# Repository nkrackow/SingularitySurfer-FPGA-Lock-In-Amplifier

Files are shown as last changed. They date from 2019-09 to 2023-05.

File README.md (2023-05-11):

# SingularitySurfer: An FPGA Lock-In Amplifier
Repository of an FPGA based DSP Lock-In Amplifier.

## Fotos:
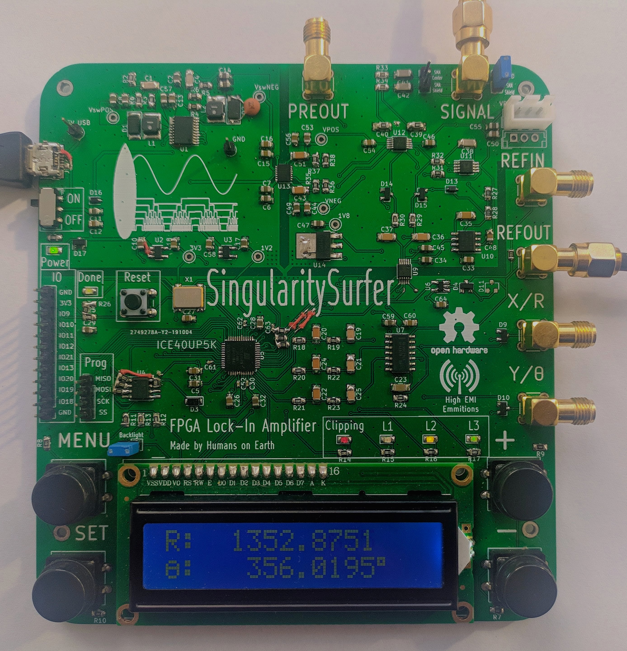
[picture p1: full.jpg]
Board front

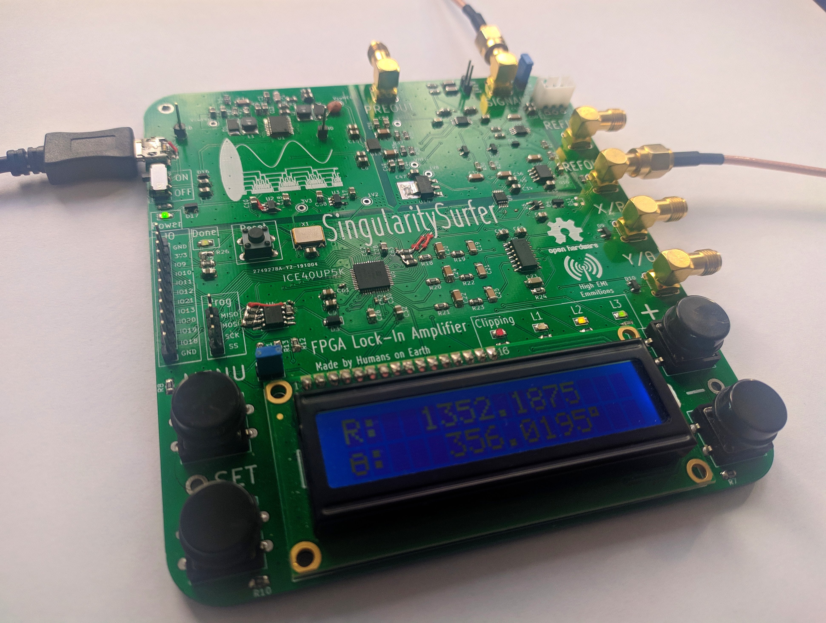
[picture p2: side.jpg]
Board sinde

Measuring the change of phase due to changing the distance of two speakers (of which one functions as a crappy microphone):
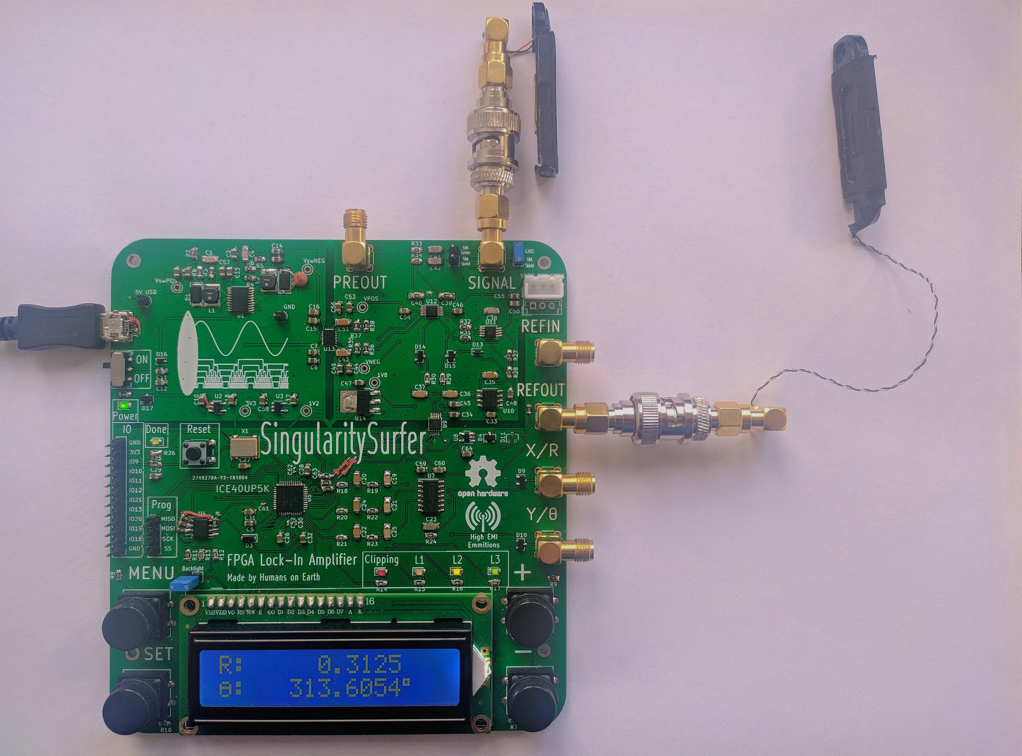
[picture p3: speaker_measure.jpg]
Measuring the change of phase due to the distance of two speakers (of which one functions as a crappy microphone)


## Block Diagram:
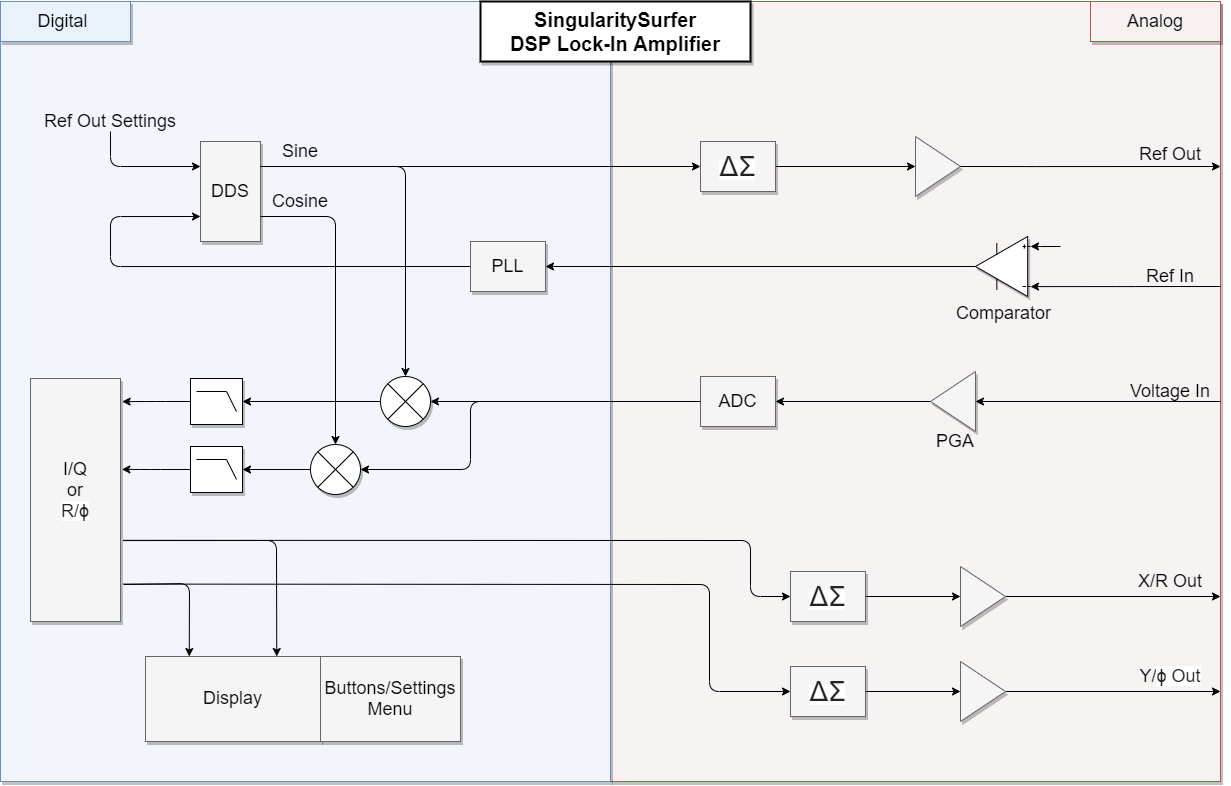
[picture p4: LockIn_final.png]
Block Diagram


## Overview:
Lock-In amplifiers are a very useful tool in many physics and bio experiments where your signal of interest might be covered by a lot of noise and interference. It does so by effectively correlating out the signal of interest. As analog components are always subject to noise, drift and non-linearities, performance in a DSP Lock-In can be far superior.
The project leverages the affordable ICE40 FPGA with its fully open source toolchain to implement the digital signal processing. Analog components are implemented in a manner that strikes a balance between performance and cost. As the analog frontend mostly determines the overall performance, a focus was put on its implementation. The total BOM cost is below 70€.
The SingularitySurfer was developed as a personal learning platform that I share so others can get design ideas and see my approach. It does not intend to give reference designs or to teach the subject. 
Cores from other people:
* CORDIC: https://opencores.org/projects/verilog_cordic_core
* SPI flash reader: https://github.com/smunaut/ice40-playground/tree/master/cores/spi_flash
* 2x16 character display driver: https://opencores.org/projects/wb_lcd

The next sections will describe the features of the various sub-systems, their development and the design decisions made.

## Digital architecture:
All of the FPGA cores run at a 36MHz base clock and the numeric oscillator, DDS, PLL and DACs also run at this sample frequency. However the ADC samples at 900kHz and the digital filters further downsample the signal by a factor of 1024. The DDS and the ADC produce signed 16 bit signals, while the output of the multipliers and filters are signed 32 bit. The phase signals from the PLL and oscillator are 18 bit. Due to FPGA LUT constraints, the CORDIC core only uses signed 16bit precision and the algorithm is terminated after 9 iterations. Most of the cores, especially the CORDIC core, make use of pipelining to maintain the 36MHz clock. The full design takes up about 85% of the FPGA LUTs.

## FPGA:
The Lattice ICE40UP5K is an ideal platform for a small DSP project like this. It offers:
* sufficient LUTs for all of the wiring, UI, display and housekeeping
* 8 16x16 hardware multipliers for signal processing
* 1Mbit of internal SRAM for storing a high fidelity sine lookup table
* QFP package which is easily soldered by hand
* affordable price at just 5€
* fully open source toolchain!

## Analog frontend:
As all of the digital signal processing is deterministic and can be upgraded at a later point, the Lock-In’s performance is ultimately determined by the analog frontend. The goal is to transfer the signal into the digital domain with little disturbance. This requires high dynamic range, low noise and high linearity. But as cost was also a factor in the development, compromises had to be made. The design employs:
* ADC: MCP33131D, 1MSps, 16bit, 91.3dB SNR 
* Voltage reference: REF5050, low noise, low drift
* PGA: AD8253, 0-60dB gain, low distortion, low noise, instrumentation amplifier
* OpAmp: AD8675, low noise
* Voltage regulator: LT3032-15, dual +-15V, low noise

At the input there is a 100kHz RC lowpass and the ADC AA filter is tuned to 100kHz as well. The PGA doubles as the ADC driver, using the AD8675 to make the signal differential. This setup was used to cut the cost of a dedicated ADC driver. Unfortunately it does limit performance, as it does introduce some distortion due to the PGA output not being fast enough to drive the ADC (which is not critical as distortion is essentially the same as noise well outside the passband of the digital lowpass). Broadband noise from the analog components was below the quantization noise and therefore not visible at the ADC output.

## DDS and numeric oscillator:
The direct digital synthesis core generates a digital representation of a sinusoidal using a 1/4 sinus look-up table stored in the 1Mbit SRAM. The other 3/4 of the sine and the cosine can be easily generated from the first 1/4 using symmetries. Therefore a high fidelity, 16bit amplitude, 18bit phase representation of the sinusoidals can be generated. When using an external reference signal, the DDS uses the phase of the digital PLL locked to the external reference signal. When generating its own reference signal, a numeric oscillator with an internal 32bit phase accumulator is employed. 
In order to avoid spurious tones in the output spectrum of the DDS when using the internal oscillator, dithering of the last phase-bit is applied using a linear-feedback shift register. Unfortunately the ICE40 SRAM blocks don't support initial values in the FPGA bitstream. Therefore the look-up table is permanently stored in the external SPI flash and loaded into SRAM after every startup.

## DAC:
As the Lock-In’s performance is not dependent on the output reference signal (as long as it contains a strong spectral component exactly at the reference frequency and other spectral components are masked by the noise added in the DUT), a basic sigma-delta DAC is used. Same goes for the X/R and Y/Theta "baseband" outputs, as they are essentially just DC (however DC accuracy has to be considered here) . The sigma-delta DACs require just a single FPGA pin and a passive second order lowpass with buffered output as external hardware in order to generate analog signals. Inside the FPGA the DAC uses a basic first-order sigma-delta modulator. With a modulator frequency of 36 MHz and 100kHz lowpass cutoff, the SNR is still better than 60dB. However switching many single-ended FPGA pins at these frequencies might lead to high EMI emissions. This was tried to be avoided by placing the lowpass filter close to the FPGA pins.

## PLL *(experimental)*:
The all-digital PLL gets a clean digital input signal by the use of a Schmitt-Trigger at the reference input. It uses a 32bit phase accumulator and 17bit phase increment word which leads to good phase precision. The DP controller can update the phase increment word without the need for multipliers by simply bit shifting the error signals. The controller can therefore only be tuned very coarsely which was done by simple trial and error. With this setup the controller can lock and track any reference signal between 500Hz and 100kHz. However it can get stuck in "limbo" with an aperiodic input signal and needs a reset to recover.

## Multipliers and CIC filter:
Twor 16x16 hardware multipliers directly "mix" the incoming ADC samples with the sine/cosine signals from the DDS core. The output is therefore a 32bit signal at ADC sampling speed. 
This signal needs to be lowpass filtered to get rid of the undesired mixing products, ideally with a very low cutoff frequency (i.e. long time-constant). At ADC sampling speed this would require a lot of memory. But as the desired signal is bandlimited to a very low frequency (10s or 100s of Hz), a high sampling rate is unnecessary. A cascaded integrator comb (CIC) filter can downsample and lowpass filter the signal at the same time. Furthermore the cutoff frequency can easily be changed in powers of two and it doesn’t require hardware multipliers. 
The downside is that the frequency response is far from an ideal lowpass. Fortunately in the case of the lock-in, this is not critical, as the cutoff frequencies are so low and the upper mixer output products are far higher than fc (it will just let more noise through which can be counteracted by a longer filter time constant). In fact right now, only a single IC stage is used in the SingularitySurfer, as there is already not enough memory for a second integrator. A good improvement would be to follow the CIC with an IIR filter using the remaining hardware multipliers.

## *(update 2020)* Multiplier less IIR filter
The SingularitySurfer was recently upgraded with a better lowpass using a very clever first order IIR filter. It uses the fact that you can multiply by a number close to 1 with bitshifting in hardware. E.g x*(15/16) can be accomplished via x-(x>>4). See [PYTHON_FILTER](https://github.com/SingularitySurfer/SingularitySurfer-FPGA-Lock-In-Amplifier/tree/master/PYTHON_FILTER) for a python demonstration.

## CORDIC:
The CORDIC algorithm computes the angle and magnitude of the sine and cosine signals. The original core by Dale Dickard was extended to support full 360 degree rotation and modified to fit into the remaining ICE40 logic. 

## Display and UI:
The display allows direct monitoring of the Lock-In outputs and user interaction with the UI. The UI is controlled via four buttons on the side of the display. This way the user can navigate through the device settings:
* Filter time constant: between 2^0 and 2^15 milliseconds
* PGA gain: 0dB, 20dB, 40dB, 60dB
* Internal/external reference 
* Internal reference frequency: 500Hz, 1kHz, 2kHz, 5kHz, 10kHz, 20kHz, 50 kHz, 100kHz
*  Internal reference output amplitude: 0.45V, 0.9V, 1.6V, 3.3V (peak to peak)

The signal monitoring can easily be switched between X/Y and R/θ view. The display is a simple 2x16 character LCD display with built-in character ROM. Unfortunately, the maximum update rate of such a display is about 2Hz. A higher update rate would lead to a more direct user feedback when monitoring signals. The logic to drive the display, show text, decimal numbers, etc., is actually not trivial and a small embedded processor could be a better idea in a future project.

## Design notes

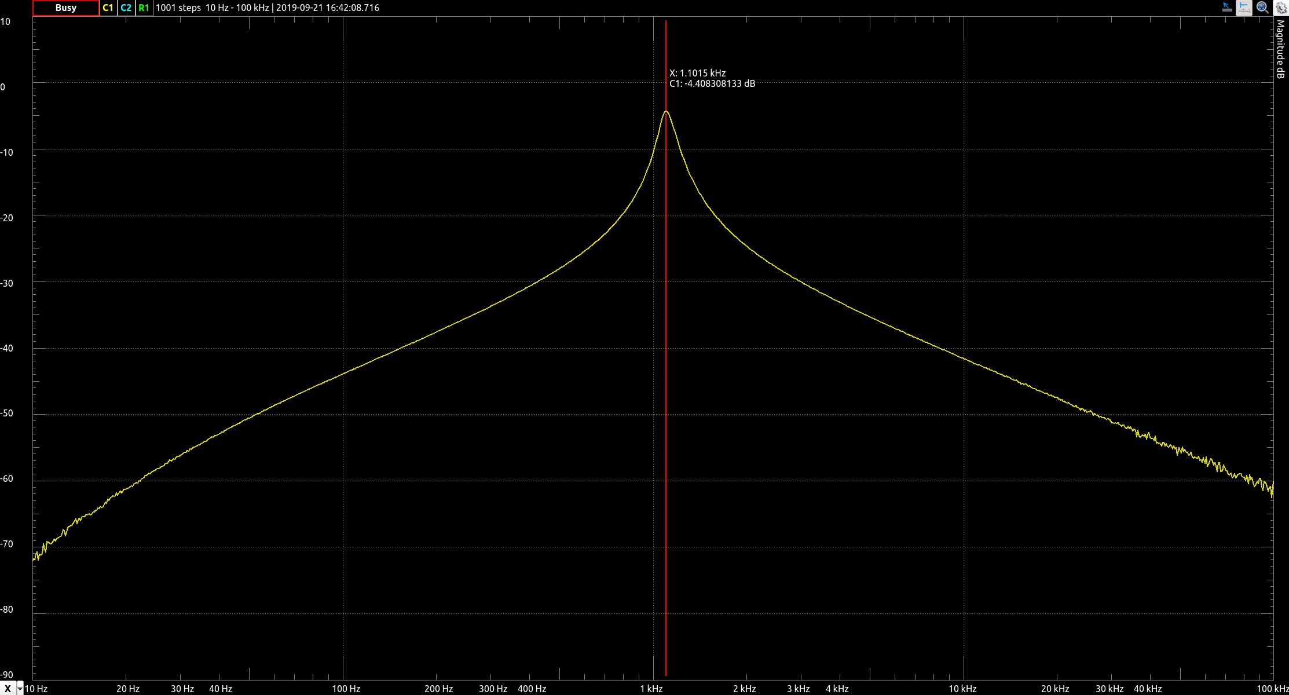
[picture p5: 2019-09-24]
WAVEFORMS/Screenshot from 2019-09-21 16-47-09.png

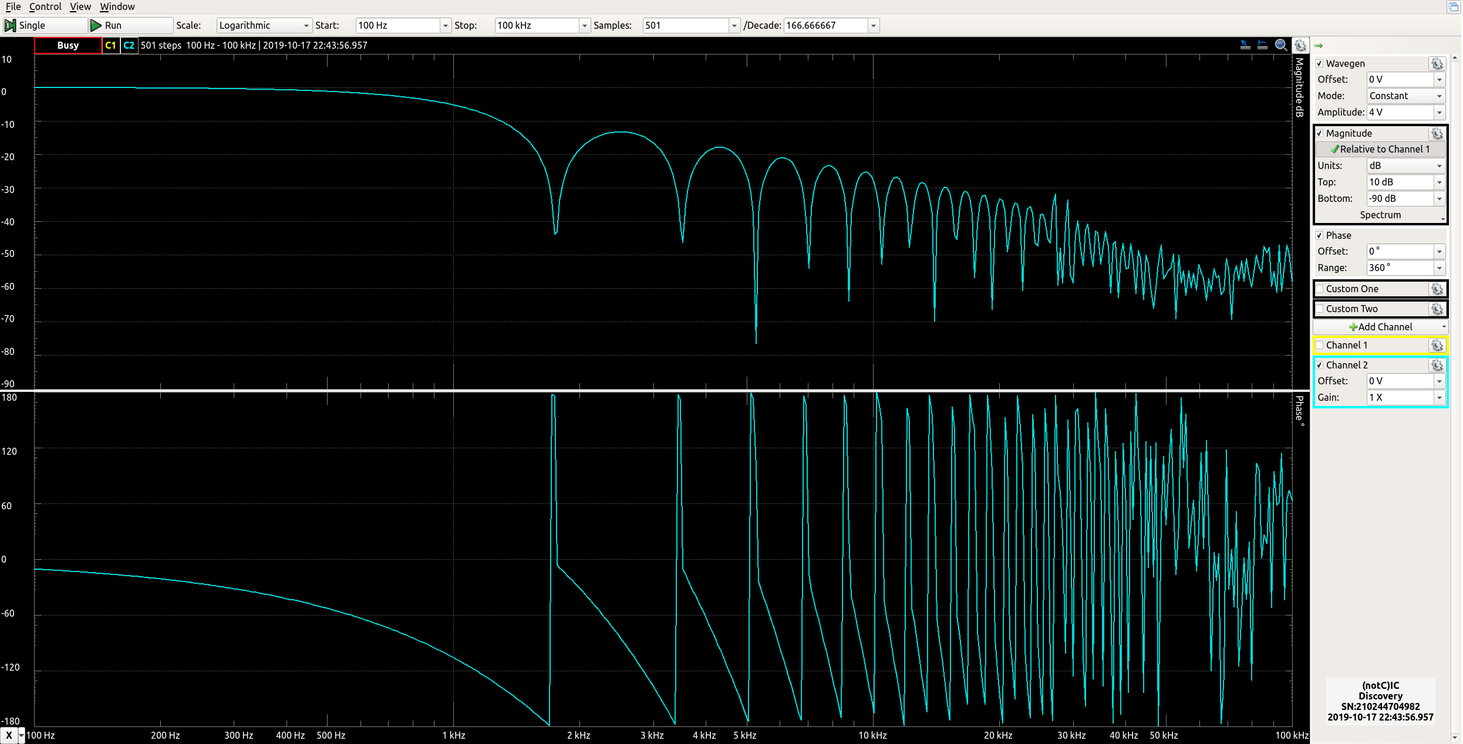
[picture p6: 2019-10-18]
WAVEFORMS/notC_I_C_filter.png

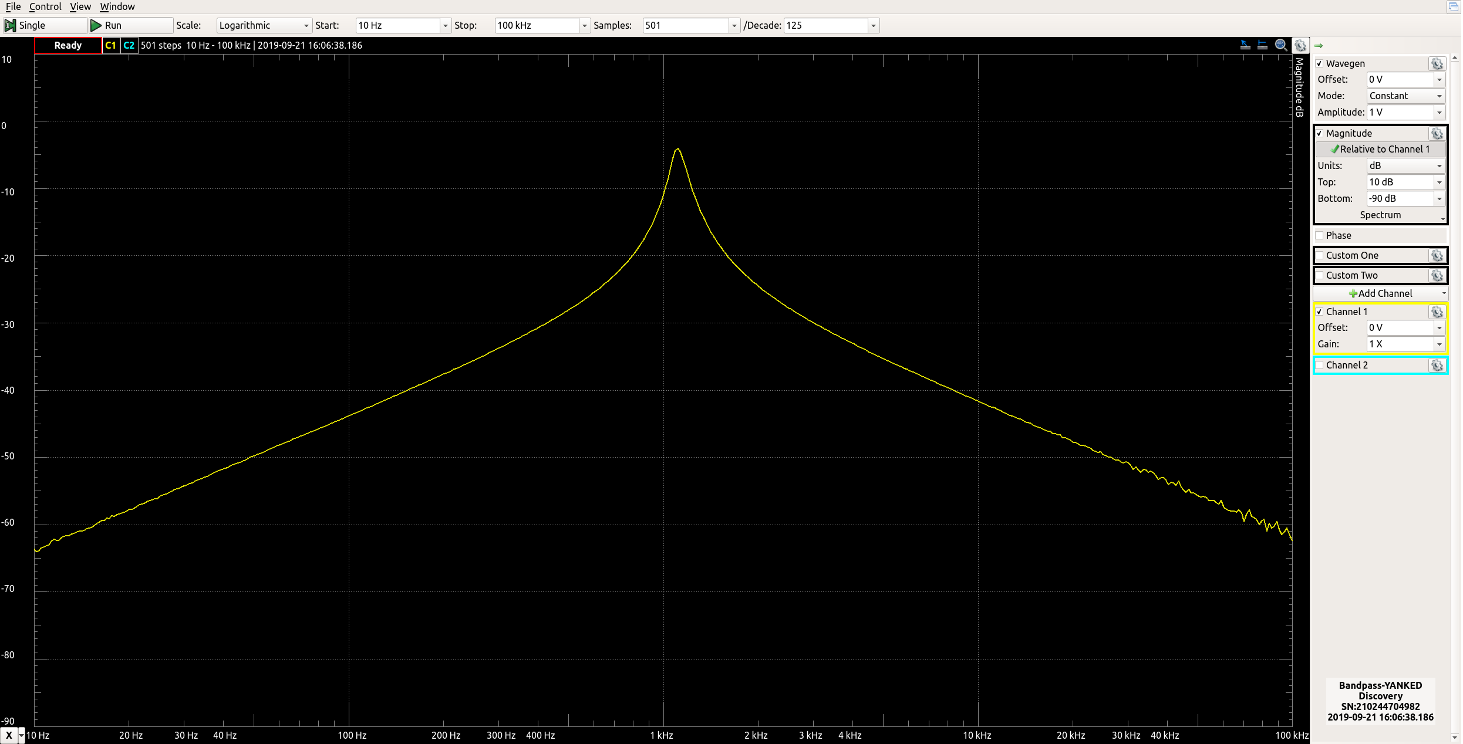
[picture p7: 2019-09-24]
WAVEFORMS/Bandpass-BAAM.png

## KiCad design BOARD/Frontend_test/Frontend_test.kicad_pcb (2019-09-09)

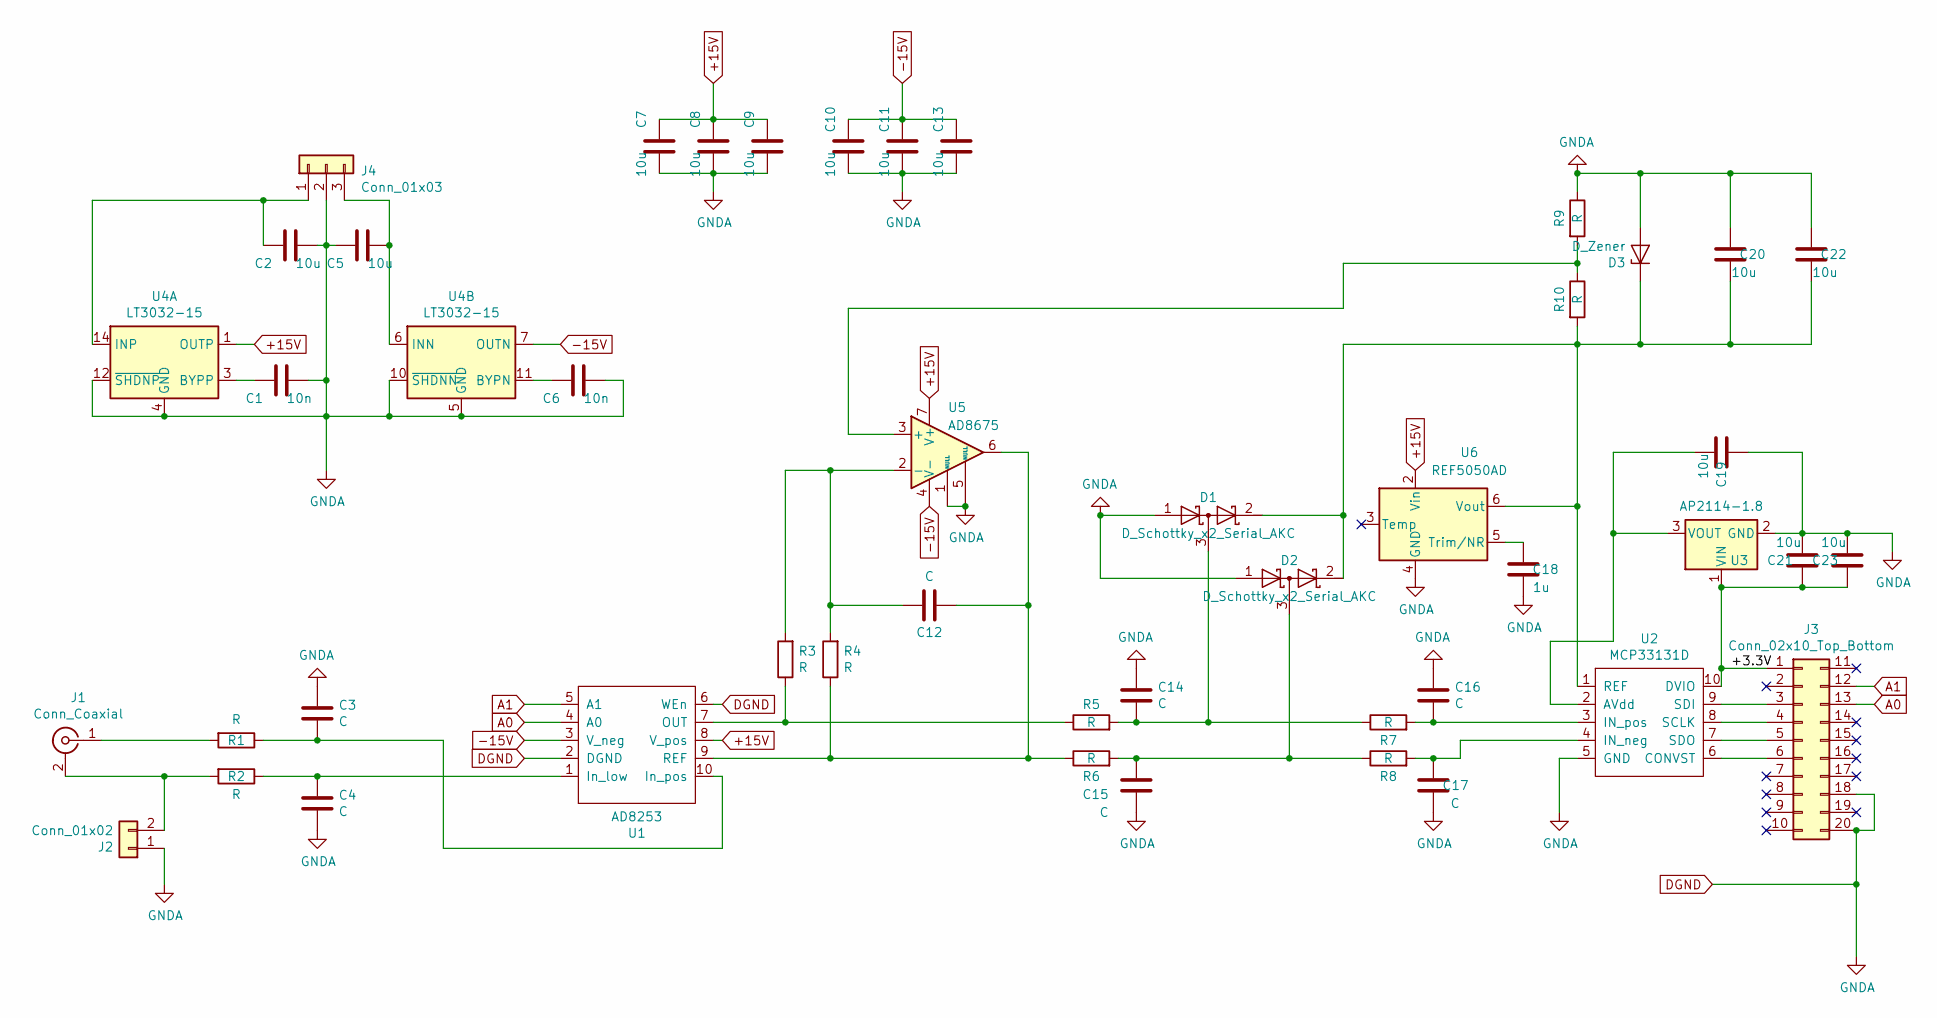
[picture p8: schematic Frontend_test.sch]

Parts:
C1, C6: 10n; C_1206_3216Metric_Pad1.42x1.75mm_HandSolder
C2, C5, C7, C8, C9, C10, C11, C13, C19, C20, C21, C22, C23: 10u; C_0805_2012Metric_Pad1.15x1.40mm_HandSolder
C3, C4, C12, C14, C15, C16, C17: C; C_1206_3216Metric_Pad1.42x1.75mm_HandSolder
C18: 1u; C_1206_3216Metric_Pad1.42x1.75mm_HandSolder
D1, D2: D_Schottky_x2_Serial_AKC; SOT-23
D3: D_Zener; D_SOD-323
J1: Conn_Coaxial; SMA_Molex_73251-2200_Horizontal
J2: Conn_01x02; PinHeader_1x02_P2.54mm_Vertical
J3: Conn_02x10_Top_Bottom; PinHeader_2x10_P2.54mm_Vertical
J4: Conn_01x03; JST_EH_B3B-EH-A_1x03_P2.50mm_Vertical
R1, R2, R3, R4, R5, R6, R7, R8, R9, R10: R; R_0805_2012Metric_Pad1.15x1.40mm_HandSolder
U1: AD8253; MSOP-10_3x3mm_P0.5mm
U2: MCP33131D; MSOP-10_3x3mm_P0.5mm
U3: AP2114-1.8; SOT-223
U4: LT3032-15; DFN-14-1EP_split_bottom_pad_3x4mm_P0.5mm_EP1.7x3.3mm
U5: AD8675; MSOP-8_3x3mm_P0.65mm
U6: REF5050AD; SOIC-8_3.9x4.9mm_P1.27mm

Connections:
+15V: C7.2, C8.2, C9.2, U1.8 (V_pos), U4.1 (OUTP), U5.7 (V+), U6.2 (Vin)
-15V: C10.2, C11.2, C13.2, U1.3 (V_neg), U4.7 (OUTN), U5.4 (V-)
/+3.3V: C21.2, C23.2, J3.1, U2.10 (DVIO), U3.1 (VIN)
A0: J3.13, U1.4 (A0)
A1: J3.12, U1.5 (A1)
DGND: C1.1, C2.1, C3.1, C4.2, C5.2, C6.1, C7.1, C8.1, C9.1, C10.1, C11.1, C13.1, C14.1, C15.1, C16.1, C17.1, C18.1, C19.2, C20.2, C21.1, C22.2, C23.1, D1.1 (A), D2.1 (A), D3.2 (A), J2.1, J3.18, J3.20, J4.2, R9.1, U1.2 (DGND), U1.6 (WEn), U2.5 (GND), U3.2 (GND), U4.4 (GND), U4.5 (GND), U4.10 (~SHDNN), U4.12 (~SHDNP), U5.1 (NULL), U5.5 (NULL), U6.4 (GND)
unnamed: C1.2, U4.3 (BYPP)
unnamed: C2.2, J4.1, U4.14 (INP)
unnamed: C3.2, R1.1, U1.10 (In_pos)
unnamed: C4.1, R2.1, U1.1 (In_low)
unnamed: C5.1, J4.3, U4.6 (INN), U4.9 (INN)
unnamed: C6.2, U4.11 (BYPN)
unnamed: C12.1, R4.1, R6.1, U1.9 (REF), U5.6
unnamed: C12.2, R3.2, R4.2, U5.2 (-)
unnamed: C14.2, D1.3 (common), R5.2, R7.1
unnamed: C15.2, D2.3 (common), R6.2, R8.1
unnamed: C16.2, R7.2, U2.3 (IN_pos)
unnamed: C17.2, R8.2, U2.4 (IN_neg)
unnamed: C18.2, U6.5 (Trim/NR)
unnamed: C19.1, U2.2 (AVdd), U3.3 (VOUT)
unnamed: C20.1, C22.1, D1.2 (K), D2.2 (K), D3.1 (K), R10.2, U2.1 (REF), U6.6 (Vout)
unnamed: J1.1 (In), R1.2
unnamed: J1.2 (Ext), J2.2, R2.2
unnamed: J3.3, U2.9 (SDI)
unnamed: J3.4, U2.8 (SCLK)
unnamed: J3.5, U2.7 (SDO)
unnamed: J3.6, U2.6 (CONVST)
unnamed: R3.1, R5.1, U1.7 (OUT)
unnamed: R9.2, R10.1, U5.3 (+)

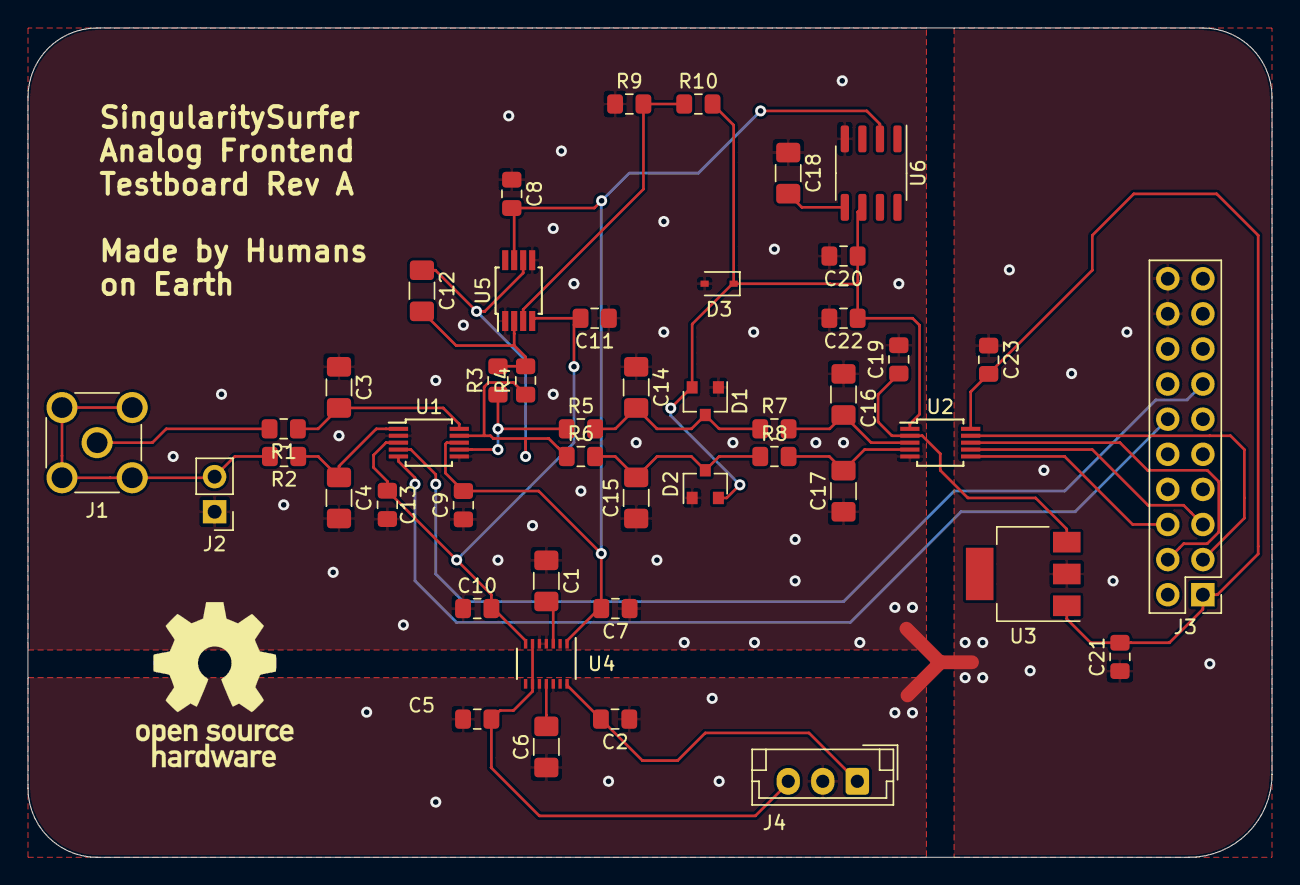
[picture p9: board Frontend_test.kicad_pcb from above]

Board: 2 copper layers, 90.0 x 60.0 mm, 46 parts (0 on the bottom side), 29 nets.

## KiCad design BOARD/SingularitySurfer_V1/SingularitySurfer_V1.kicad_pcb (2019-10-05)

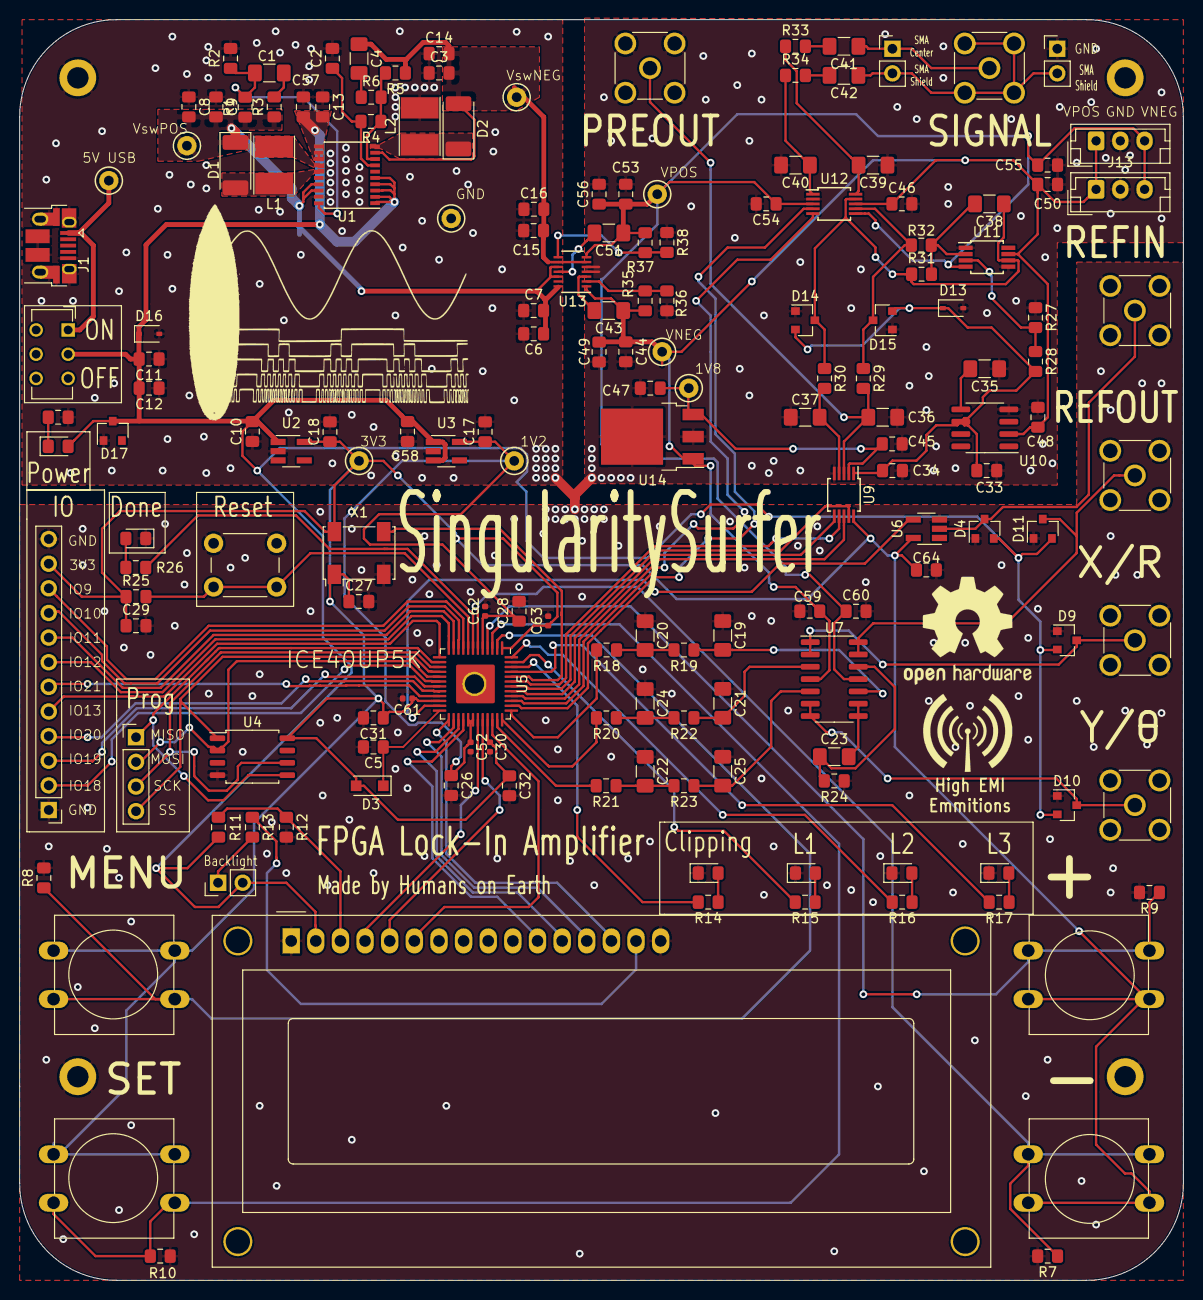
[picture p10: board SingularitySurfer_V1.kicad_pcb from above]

Board: 2 copper layers, 120.0 x 130.0 mm, 171 parts (0 on the bottom side), 99 nets.

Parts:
 : TestPoint; TestPoint_Keystone_5000-5004_Miniature
 #2,  #3,  #4,  #5: MountingHole_2.2mm_M2_DIN965_Pad
 #6: Conn_01x02_Male; PinHeader_1x02_P2.54mm_Vertical
 #7: Conn_01x12; PinHeader_1x12_P2.54mm_Vertical
 #8: Conn_01x04_Male; PinHeader_1x04_P2.54mm_Vertical
 #9,  #12,  #13,  #14,  #15,  #16,  #17,  #18: TestPoint; TestPoint_Keystone_5000-5004_Miniature
 #10: R; R_0805_2012Metric_Pad1.15x1.40mm_HandSolder
 #11: Conn_01x03; JST_EH_B3B-EH-A_1x03_P2.50mm_Vertical
 #19,  #20,  #21,  #22,  #23,  #24: LED; LED_0805_2012Metric_Pad1.15x1.40mm_HandSolder
 #25,  #27,  #30,  #31,  #32,  #33: Conn_Coaxial; SMA_Molex_73251-2200_Horizontal
 #26: SW_Push; SW_PUSH_6mm
 #28,  #29: Conn_01x02; PinHeader_1x02_P2.54mm_Vertical
 #34: WC1602A
 #35: SW_DIP_x01; SW_CuK_JS202011AQN_DPDT_Angled
+1: SW_Push; SW_PUSH-12mm
-1: SW_Push; SW_PUSH-12mm
C1, C4, C19, C20, C21, C22, C23, C24, C25, C36, C37, C38, C39, C40, C41, C42, C43, C51: C; C_1206_3216Metric_Pad1.42x1.75mm_HandSolder
C2, C3, C5, C6, C7, C8, C9, C10, C11, C12, C13, C14, C15, C16, C17, C18, C26, C27, C28, C29, C31, C32, C44, C45, C46, C47, C48, C49, C50, C53, C54, C55, C56, C57, C58, C59, C60, C64: C; C_0805_2012Metric_Pad1.15x1.40mm_HandSolder
C30, C52, C61, C62, C63: C; C_0402_1005Metric
C33, C34: 10u; C_0805_2012Metric_Pad1.15x1.40mm_HandSolder
C35: 1u; C_1206_3216Metric_Pad1.42x1.75mm_HandSolder
D1, D2: D; D_2010_5025Metric_Pad1.52x2.65mm_HandSolder
D3: D; D_SOD-123F
D4, D9, D10, D11, D14, D15, D17: D_Schottky_x2_Serial_AKC; SOT-23
D13, D16: D_Zener; D_SOD-323
J1: USB_B_Micro; USB_Micro-B_Amphenol_10103594-0001LF_Horizontal
J13: Conn_01x03; JST_EH_B3B-EH-A_1x03_P2.50mm_Vertical
L1, L2: INDUCTOR; L_Taiyo-Yuden_NR-40xx_HandSoldering
MENU1: SW_Push; SW_PUSH-12mm
R1, R2, R3, R4, R5, R6, R7, R8, R9, R10, R11, R12, R13, R14, R15, R16, R17, R18, R19, R20, R21, R22, R23, R24, R25, R26, R27, R28, R29, R30, R31, R32, R33, R34, R35, R36, R37, R38: R; R_0805_2012Metric_Pad1.15x1.40mm_HandSolder
SET1: SW_Push; SW_PUSH-12mm
U1: BD81870EFV; SSOP-20_4.4x6.5mm_P0.65mm
U2: MIC5504-3.3YM5; SOT-23-5_HandSoldering
U3: TLV70212_SOT23-5; SOT-23-5_HandSoldering
U4: W25Q32JVSS; SOIC-8_5.23x5.23mm_P1.27mm
U5: ICE40UP5K-SG48ITR; QFN-48-1EP_7x7mm_P0.5mm_EP5.6x5.6mm
U6: 74LVC1G17; SOT-23-5_HandSoldering
U7: OPA1679; SOIC-14_3.9x8.7mm_P1.27mm
U9: MCP33131D; MSOP-10_3x3mm_P0.5mm
U10: REF5050AD; SOIC-8_3.9x4.9mm_P1.27mm
U11: AD8675; MSOP-8_3x3mm_P0.65mm
U12: AD8253; MSOP-10_3x3mm_P0.5mm
U13: LT3032; DFN-14-1EP_split_bottom_pad_3x4mm_P0.5mm_EP1.7x3.3mm
U14: AP2114-1.8; TO-252-3_TabPin2
X1: DFA-S11; Oscillator_SMD_Fordahl_DFAS11-4Pin_7.0x5.0mm

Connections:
1V2: #12.1, C17.1, C26.1, C28.1, C52.1, C62.1, U3.5, U5.5, U5.29, U5.30
1V8: #16.1, C45.1, C47.1, U9.2, U14.3
3V3: #7.11, #9.1, +1.2, -1.2, C18.1, C27.1, C29.1, C30.1, C31.1, C32.1, C61.1, C63.1, C64.1, D3.2, MENU1.2, R25.1, SET1.2, U2.5, U4.8, U5.1, U5.22, U5.33, U6.5, U9.10, X1.1, X1.4
5V: #6.2, #19.2, #34.2, #35.2, C10.2, C11.2, C12.2, C13.2, C57.2, C58.2, D4.2, D9.2, D10.2, D11.2, D16.1, D17.3, R11.1, U1.1, U1.2, U1.3, U1.4, U1.5, U1.11, U1.12, U1.13, U2.1, U3.1, U3.3
+8V: #11.1, #15.1, C43.1, C44.1, C46.1, C48.1, C49.1, C50.1, C59.1, J13.1, R35.2, U7.4, U10.2, U11.7, U12.8, U13.1, U14.1
-8V: #11.3, #13.1, C51.1, C53.1, C54.1, C55.1, C56.1, C60.1, J13.3, R37.2, U7.11, U11.4, U12.3, U12.6, U13.7
/Power/VNEG: #14.1, C3.2, C4.1, C14.2, C15.2, C16.2, D2.2, R5.1, U1.9, U13.6, U13.9
A0: U5.38, U12.4
A1: U5.39, U12.5
CDONE: R26.2, U5.7
CONVST: U5.41, U9.6
GND: .1, #2.1, #3.1, #4.1, #5.1, #7.1, #7.12, #10.1, #11.2, #20.1, #21.1, #22.1, #23.1, #24.1, #25.2, #26.1, #28.1, #30.2, #31.2, #32.2, #33.2, #34.1, #34.16, C2.2, C3.1, C5.2, C6.1, C7.1, C8.1, C9.1, C10.1, C11.1, C12.1, C13.1, C14.1, C15.1, C16.1, C17.2, C18.2, C19.1, C20.1, C21.1, C22.1, C24.1, C25.1, C26.2, C27.2, C28.2, C29.2, C30.2, C31.2, C32.2, C33.2, C34.2, C35.1, C36.1, C37.1, C39.1, C40.2, C44.2, C45.2, C46.2, C47.2, C48.2, C49.2, C50.2, C52.2, C53.2, C54.2, C55.2, C56.2, C57.1, C58.1, C59.2, C60.2, C61.2, C62.2, C63.2, C64.2, D4.1, D9.1, D10.1, D11.1, D13.2, D14.1, D15.1, D16.2, D17.1, J1.5, J1.6, J13.2, L2.2, R2.2, R7.2, R8.2, R9.2, R10.2, R12.2, R24.1, R27.1, R36.1, R38.1, U1.16, U1.19, U2.2, U3.2, U4.4, U5.49, U6.3, U9.5, U10.4, U11.1, U11.5, U12.2, U13.4, U13.5, U14.2, X1.2
unnamed: +1.1, R9.1, U5.4
unnamed: -1.1, R7.1, U5.6
unnamed: C1.1, R3.2
unnamed: C1.2, R1.2, R2.1, U1.20
unnamed: C2.1, R4.2, U1.7
unnamed: C4.2, R6.1
unnamed: C5.1, D3.1, U5.24
unnamed: C19.2, R19.1, U7.10
unnamed: C20.2, R18.1, R19.2
unnamed: C21.2, R22.1, U7.3
unnamed: C22.2, R21.1, R23.2
unnamed: C23.1, R24.2, U7.12
unnamed: C23.2, U7.8, U7.9
unnamed: C24.2, R20.1, R22.2
unnamed: C25.2, R23.1, U7.5
unnamed: C33.1, C34.1, D13.1, D14.2, D15.2, R28.2, U9.1, U10.6
unnamed: C35.2, U10.5
unnamed: #25.1, C36.2, R29.2, U9.3
unnamed: C37.2, R30.2, U9.4
unnamed: C38.1, D14.3, R30.1, R31.1, U11.6, U12.9
unnamed: C38.2, R31.2, R32.2, U11.2
unnamed: C39.2, R33.1, U12.10
unnamed: C40.1, R34.1, U12.1
unnamed: #27.1, #29.1, C41.1
unnamed: C41.2, R33.2
unnamed: #27.2, #28.2, #29.2, C42.1
unnamed: C42.2, R34.2
unnamed: C43.2, U13.3
unnamed: C51.2, U13.11
unnamed: D1.2, L1.1, U1.15
unnamed: D2.1, L2.1, U1.10
unnamed: #33.1, D4.3, U6.2
unnamed: #24.2, R14.1
unnamed: #23.2, R15.1
unnamed: #22.2, R16.1
unnamed: #21.2, R17.1
unnamed: #31.1, D9.3, U7.1, U7.2
unnamed: #30.1, D10.3, U7.6, U7.7
unnamed: #32.1, D11.3, U7.13, U7.14
unnamed: #20.2, R26.1
unnamed: D15.3, R29.1, R32.1, U12.7
unnamed: #10.2, #19.1
unnamed: #34.3, R11.2, R12.1
unnamed: #34.4, U5.31
unnamed: #34.5, U5.32
unnamed: #34.6, U5.34
unnamed: #34.11, U5.28
unnamed: #34.12, U5.27
unnamed: #34.13, U5.26
unnamed: #34.14, U5.25
unnamed: #34.15, R13.1
unnamed: #17.1, #35.1, J1.1
unnamed: #8.1, U4.5, U5.14
unnamed: #8.2, U4.2, U5.17
unnamed: #8.3, U4.6, U5.15
unnamed: #8.4, U4.1, U5.16
unnamed: #7.2, U5.18
unnamed: #7.3, U5.19
unnamed: #7.4, U5.20
unnamed: #7.5, U5.13
unnamed: #7.6, U5.21
unnamed: #7.7, U5.12
unnamed: #7.8, U5.11
unnamed: #7.9, U5.10
unnamed: #7.10, U5.9
unnamed: #6.1, R13.2
unnamed: L1.2, U1.14
unnamed: MENU1.1, R8.1, U5.2
unnamed: R4.1, R5.2, R6.2, U1.8
unnamed: R10.1, SET1.1, U5.3
unnamed: R14.2, U5.46
unnamed: R15.2, U5.47
unnamed: R16.2, U5.48
unnamed: R17.2, U5.45
unnamed: R18.2, U5.37
unnamed: R20.2, U5.36
unnamed: R21.2, U5.35
unnamed: R27.2, R28.1, U11.3
unnamed: R35.1, R36.2, U13.2
unnamed: R37.1, R38.2, U13.8
unnamed: U5.23, U6.4
unnamed: U5.44, X1.3
SCLK: U5.40, U9.8
SDI: U5.42, U9.9
SDO: U5.43, U9.7
VPOS: #18.1, C6.2, C7.2, C8.2, C9.2, D1.1, R1.1, R3.1, U1.17, U1.18, U13.10, U13.12, U13.14
nCRESET: #26.2, R25.2, U5.8

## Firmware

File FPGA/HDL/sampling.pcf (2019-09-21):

set_io CLK12 37   # Bridged from pin 35!!! pnr fails with 35 as input to PLL


# RGB LED
set_io R 41
set_io G 40
set_io B 39

# Header C outside +v inside

set_io sMISO 47
set_io sMOSI 44
set_io sSCLK 46
set_io sCS 2



# ADC interfaces

set_io SDI 23         #37A
set_io SCLK 26        #39A
set_io SDO 25         #36B
set_io CONVST 36      #48B
set_io GAIN_A1 38     #50B
set_io GAIN_A0 31     #42B



# Switches
set_io S[0] 43
set_io S[1] 34

# SPI flash
set_io ss   16
set_io miso 17
set_io mosi 14
set_io sck  15

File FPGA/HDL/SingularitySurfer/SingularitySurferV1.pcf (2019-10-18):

#  Constrain File for the Singularity Surfer V1 board



# Clock input from external 36 MHz Oscillator
set_io CLK36 44



# LED
set_io L0 46           # clipping LED
set_io L1 47           # L1
set_io L2 48           # L2
set_io L3 45           # L3



#Buttons
set_io SET 3           # Button SET
set_io PLUS 4          # Button +
set_io MENU 2          # Button MENU
set_io MINUS 6         # Button -



#Analog Outputs
set_io X_R 36         # X or R(magnitude) output
set_io Y_T 35         # Y or Theta output
set_io REFOUT 37      # Y or Theta output



# Reference Input
set_io REFIN 23       # Reference input from SMA over a Schmitt trigger


# ADC Interface
########################################################################
# DIFFERENT THAT ON SCHEMATIC!!   SWITCHED BC OF OPEN DRAIN LED PINS (too slow for adc spi)
set_io SCLK 38        # SPI clock       SWITCHED WITH A0!!!!!!!!!!
set_io CONVST 42      # ADC start converion signal    SWITCHED WITH SDI
set_io SDI 41         # ADC serial input (not used right noe)     SWITCHED WITH CONVST
########################################################################
set_io SDO 43         # ADC serial out




# PGA Interface
#######################################################################
# DIFFERENT THAT ON SCHEMATIC!!   SWITCHED BC OF OPEN DRAIN LED PINS (too slow for adc spi)
set_io A0 40         # PGA gain pin 0     SWITCHED WITH SCLK!!!!!
########################################################################
set_io A1 39         # PGA gain pin1



# LCD Interface
set_io LCD_E 34            # LCD enable
set_io LCD_RW 32           # LCD read/write
set_io LCD_RS 31           # LCD register select
set_io LCD_D4 28           # LCD Data Pin 4
set_io LCD_D5 27           # LCD Data Pin 5
set_io LCD_D6 26           # LCD Data Pin 6
set_io LCD_D7 25           # LCD Data Pin 7



# IO Header
set_io IO[0] 9             # IO Header Pin 0 (IO9)
set_io IO[1] 10            # IO Header Pin 1 (IO10)
set_io IO[2] 11            # IO Header Pin 2 (IO11)
set_io IO[3] 12            # IO Header Pin 3 (IO12)
set_io IO[4] 21            # IO Header Pin 4 (IO21)
set_io IO[5] 13            # IO Header Pin 5 (IO13)
set_io IO[6] 20            # IO Header Pin 6 (IO20)
set_io IO[7] 19            # IO Header Pin 7 (IO19)
set_io IO[8] 18            # IO Header Pin 8 (IO18)



# SPI Flash Interface
set_io SS 16               # SPI Slave Select
set_io SCK 15              # SPI Serial Clock
set_io SO 14               # SPI Serial Output
set_io SI 17               # SPI Serial Input

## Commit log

2019-09-09 Analog Frontend Testboard designed and out in Production :)
    [Frontend_test-B_Cu.gbr, Frontend_test-B_Mask.gbr, Frontend_test-B_Paste.gbr, Frontend_test-B_SilkS.gbr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]
2019-09-21 finished the analog frontend testboard and the fpga sampling hardware. The FPGA samples into the internal SRAM and then transfers the data via serial to the analog discovery. the AD is scripted to re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
2019-09-24 Power Supply Section of final Board done
    [Frontend.sch, Power.sch, SingularitySurfer_V1.kicad_pcb, SingularitySurfer_V1.sch]
2019-09-26 More work on final Schematic. Power, digital and output section close to final. No frontend yet.
    [Frontend.sch, Power.sch, SingularitySurfer_V1.kicad_pcb, SingularitySurfer_V1.sch]
2019-09-29 Final Board schematic almost done and started on layout
    [Frontend.sch, Power.sch, SingularitySurfer_V1.kicad_pcb, SingularitySurfer_V1.sch]
2019-10-03 SignularitiSurfer final boar almost donegit status! Fuuuak this is getting rediculous...
    [Frontend.sch, Power.sch, SingularitySurfer_V1.kicad_pcb, SingularitySurfer_V1.sch]
2019-10-05 Final board done, plotted and in production. Started on LCD driver, already working with scrolling HI :)
    [Power.sch, SingularitySurfer_V1-B_Cu.gbr, SingularitySurfer_V1-B_Mask.gbr, SingularitySurfer_V1-B_Paste.gbr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]
2019-10-14 Board fully assembled over the course of like 50 hours... SO much PAIIIN.. BUT IT FUCKING WOOOORKS :) wrote some testcode for buttons and leds. frontend testing next!
2019-10-18 lots of work on various topics. Lots of board and filter testing, dds on the SS board and now working on CORDIC but not working yet due to timing..
2019-10-21 lots of final work like PLL integrated, UI implementation, tweaks etc. Filter not working with big Ratechange yet...
2020-06-12 idiot me forgot to push final changes half a year ago.. Fixed code: filter constant 3 bit, filter downsampling factor and some mics. Converted KiCad stuff to new version
    [Frontend.sch, Power.sch, SingularitySurfer_V1.sch]
2020-06-13 python script for multiplier-less IIR filter
2020-06-16 added RIIR filter in migen. gets converted to verilog by makefile and integrated in the top module. also some more minor tweaks.
